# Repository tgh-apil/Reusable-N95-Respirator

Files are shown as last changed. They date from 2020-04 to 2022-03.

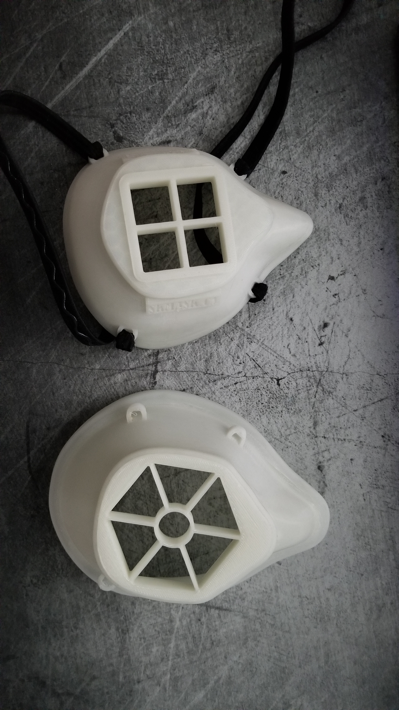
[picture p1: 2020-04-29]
02-Design Types/USask MontanaMask Mods/Photos/20200426_123736.jpg

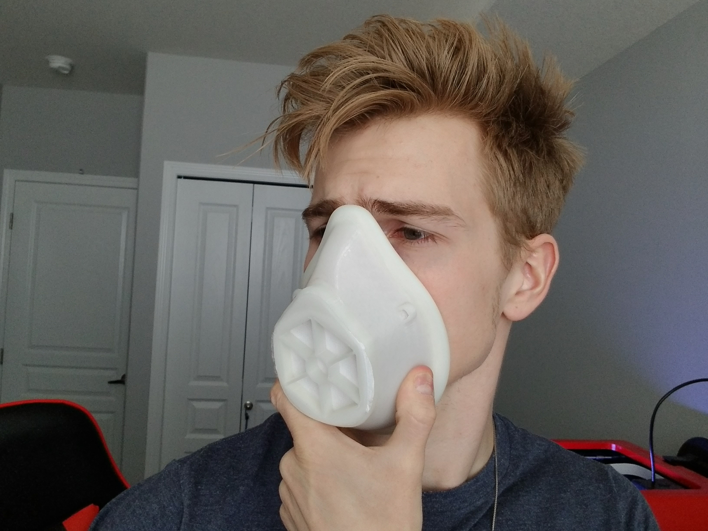
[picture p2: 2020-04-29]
02-Design Types/USask MontanaMask Mods/Photos/20200427_112252.jpg

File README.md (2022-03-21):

# Reusable N95 Respirator
An open-source, reusable N95 respirator that can be manufactured at scale in small community or hospital-based facilities, using 3D printing, silicone casting and standard HME filters.

Developed at the [Lynn & Arnold Irwin Advanced Perioperative Imaging Lab, Toronto General Hospital](https://apil.ca).

# DISCLAIMER
This is an **INVESTIGATIONAL MEDICAL DEVICE** being evaluated for use
in hospital setting during **extreme crisis** leading to N95
shortages.

It has **not been approved** by any regulatory body.

Its use is **not endorsed** by any institution or professional body,
including the ones where it was developed and tested.

We have made every effort to make the system as safe as possible and to
provide documentation and educational materials for its use, should it be
necessary, in order to minimize the very significant risks of iatrogenic harm.

It is posted here in order to facilitate rapid knowledge sharing and research
on strategies for addressing the global ventilator shortages.

Any of use of this device is done purely at your own risk and liability. The
developers and associated institutions do not accept any liability for its use.

# Publications & Media
1. [Anwari V, Ng WCK, Mbadjeu Hondjeu AR, Xiao Z, Afenu E, Trac J, Kazlovich K, Hiansen J, Mashari A. Development, manufacturing, and preliminary validation of a reusable half-face respirator during the COVID-19 pandemic. PLoS One. 2021;16(3):e0247575.](https://doi.org/10.1371/journal.pone.0247575) 
2. [Ng WCK, Hondjeu ARM, Syrett A, Caragata R, Rozenberg D, Xiao Z, Anwari V, Trac J, Mashari A. Subject validation of reusable N95 stop-gap filtering facepiece respirators in COVID-19 pandemic. PLOS ONE. 2020 Nov 13;15(11):e0242304.](https://doi.org/10.1371/journal.pone.0242304) 
3. [OCI VIP Funding Reusable N95 Respirator Report in Collaboration with TME Inc. 2021-2022](https://hackmd.io/2YckHMyaT0aIxTetDs7KHw)

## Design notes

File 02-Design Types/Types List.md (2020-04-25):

Orig: Will Ng

Last: 17 April 2020

Still nothing FDA of HC approved

# Short-list criteria
1) Open Source, licence to use and refine
2) 3D printable with available printers (to us)
3) Clinically tested 
4) Theoretically decontaminable easily
5) Theoretically suitable for long-hours wear

# Short-List
### NIH released open sources
- https://3dprint.nih.gov/collections/covid-19-response; currently only one on NIH exchange that is clinically reviewed.
- https://3dprint.nih.gov/discover/3dpx-013429 NIH "SFM" Mask is clinically tested
- many variations to choose from, apart form the above, which have gained traction and use in several hospitals
- Now modified by APIL to unibody Silicone Mould, awaiting testing.

### Simple Silicone Respirator by Christian Petropolis at HSC Manitoba
- silicone material dragon skin sx pro to 10, durometer 2A - 10
- attaches to commerical filters 15mm to 22mm
- M size fits small to large
- working copy https://cad.onshape.com/documents/a5f5de31c4732fb3c077f7d9/w/7b1df48439473aaa39a18cc3/e/e7b3ab7f8894425fe0ec1df3
- original cad https://cad.onshape.com/documents/912751c654360860ae260334/w/75644efc74b9616c5ac20c2f/e/7fecc2776bb556dd9c7c6a62
- https://github.com/cpetropolis/Simple-Silicone-Respirator

### "Kingston" Mask - Queen's Initiative
- http://ppekingston.squarespace.com/
- Modification of Montana with different sizing, filter size, geometry
- fit-testing done by OSH at KGH

### Barrow Neurosurgery
- https://www.barrowneuro.org/get-to-know-barrow/barrow-innovation-center-2/3d-printed-n95-mask/
- Montana with silicone gasket and adapter for large 3M 2000 P100 filter type

### Billings, Montana
- https://www.makethemasks.com
- tested and used Billings Clinic, MT; ? in Utah; Kaiser San Diego;

### Intermountain3D - modified Montana with flat rim
- https://www.intermountain3d.com/covid-respirators.html
- ask about files: SLS printing and assembly, lynn@intermountain3d.com

_____
## Interesting downward facing filter with screw/lock mechanism.
- https://copper3d.com/hackthepandemic/

## Other-list
- Concordia (Modified Montana) respirator mask
- https://blog.cuw.edu/access-concordias-respirator-mask-3d-print-file/
- has double inner rim, suitable for silicone/rubber gasket seal

- Basic Respirator Tyvek flat filter
- https://basicrespirator.com

## Design Partners
- Nadir Hassan, Nadir.Hassan002@gmail.com
- Jessica Schroeder, Jessica.Laura.Shcroeder@gmail.com
_____

## Government statements
FDA:
"https://www.fda.gov/medical-devices/3d-printing-medical-devices/faqs-3d-printing-medical-devices-accessories-components-and-parts-during-covid-19-pandemic"

HC: 
https://www.canada.ca/en/health-canada/services/drugs-health-products/medical-devices/covid-19-unconventional-manufacturing-personal-protective-equipment.html

CDC: 
https://www.cdc.gov/coronavirus/2019-ncov/hcp/respirators-strategy/index.html

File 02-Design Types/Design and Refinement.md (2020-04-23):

Orig: Will Ng
Last: 2020-04-21
Title: Designs and Refinements

## Manitoba Tasks
1. Harness bent-like-stool Print with cirular buttons (Arash)
2. Reduced Bottom island (Natasha)
3. All original files converted to STEP (Natasha)
4. Strap Moulds (James from Vertigro)
5. Silicone Casting (Josh and Vahid)

### Manitoba Parts
1. Manitoba Flat Harness Mould: https://a360.co/3cCDOWk (Arash)
2. Manitoba Middle Mould enlarged: https://a360.co/2xBQWfM, 2nd part file https://a360.co/2RRTo8u (Will's fault, Natasha)

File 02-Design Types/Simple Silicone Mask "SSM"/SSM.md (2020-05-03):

Orig: Will Ng
Title: Simple Silicone Mask *aka* "SSM"
Last: 2020 May 3

# Simple Silicone Mask, attribution "SSM"
## Name - "SSM"
- For simplicity we'll name this mask body design and derivatives SSM Simple Silicone Mask
- It is a branch off the Simple Silicone Respirator, which we have called "SSR"
- By itself the "SSM" body is just a mask
- A fitting filter then makes it a Respirator
- We see the future of this stop-gap solution as modular: one mask body can accommodate additional modules

# Ideas for Derviatives
## Dual Filter Cartridge
- If DAR and Intersurgical medical filters are depleted
- Having Modular FIlter solutions means we can adapt to multiple filters that can be sourced.

## Expiratory Valve
- Greatly reduces condensation, heat trap and thus improves wearer comfort
- All valves be potentially be designed with a filter so that the atmospheric air mixture droplets/particles 
is separate from inner air mixture droplets/particles.
- Awaiting Dr. Sameer Masood's design of expiratory valve with filter that can be fitted to non-rebreather masks.

## Integrated Harness
- The harness may be integrated into the body

SSM License is under the Project CERN 2.0 License so that all remain "open".

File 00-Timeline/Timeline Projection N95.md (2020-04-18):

Orig: Will Ng

Last: 17 Apr 2020

# TIMELINE for Reusable N95 Project

- Project Manager: Nasa Nguyen
- Partners: APIL, CIGITI, Lakehead, NOSM, Queen's, SickKids Anes, GLIA, UofT 3DP-GTHA, ~Brian~ (Industry)

### Lead up from 6 Apr 2020 
- NIH S, M Moulds by 10am 13 Apr 2020 [Brandon CIGITI/Will]
- Montana S, M by 10am 13 Apr 2020 [Brandon CIGITI/Will]
- NIH S, M Inlays by 10am 13 Apr 2020 [Josh/Vahid]
- see summaries and minutes on MatterMost https://group.emlondon.ca ~ "Respirator Masks"
- Choose 3 Mask bodies [Will/Andrew/Brandon/Josh/Vahid] 8pm 13 Apr 2020

### Week 1 - 13 Apr 2020
- NIOSH Testing @ 11am 13 Apr [Andrew/Vahid] [Lead/Assist]
- Adapter with slightly smaller connection to ROXON for NIH and Montana [Josh] by 14 Apr
- Bitrex Testing for 3 sizes of 1 type by 17 Apr [Andrew/Queen's]
- Bitrex Testing UHN [Will/Azad] by TBC as barriers expected
- REB [Binu/Jo Carroll] by 16 Apr
- Ontario Power Generation testing facilities [Leah|Queen's], floating
- Candidate Refining [Josh/Vahid/Brandon/Taylor] 16 Apr 
- Arrange 2nd NIOSH after refinement 17 Apr [Josh/Vahid/Brandon/Taylor]

### Week 2 - 20 Apr 2020 [Surge Week, expect Andrew, Will, Azad down]
- Decontamination Protocols [Vahid/GLIA]
- Need GLIA's help with MDEL or APIL's MDEL [Azad/GLIA]
- Health Canada approval [Azad/GLIA]
- Industry for upscale of Silicone Moulds, Bodies, [Will/Brian]
- Filtering solution from Woodbridge (if filter passes) [Will]
- First 10 units [Brian/Will]
- Test first 10 Units [Vahid/GLIA]

### Week 3 - 27 Apr 2020 [Surge Week]
- First 25 units [Brian/Will]
- Test batches [Vahid/GLIA]
- Website [other]
- Logistics [GLIA/Will]
- Dissemination of Information to interested centres [Andrew]

### Week 4 - 4 May 2020 [Surge Week]
- First 100 units [Brian/Will]
- UHN Stock for stop-gap [Will/Azad]
- Project wind-down [Will/GLIA] 
- Write-up [Andrew/Will]

### Week 5 to 8 [depending on ongoing funding]
- Reassess [All]

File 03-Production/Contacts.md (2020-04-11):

Orig: Will Ng
Last: 10 April 2020

## Materials Science
Yu Zou, PhD
- mse.zou@utoronto.ca
- Dept Materials Science and Engineering

## CIGITI, SickKids
Thomas Looi, PhD, MBA
- thomas.looi@sickkids.ca

## UHN
Tina Meisami
- tina.meisami@uhn.ca
- Sewable Mask Development

## Ostrom Medical Engineering
Devon Ostrom
- list of laser cutters and small DYI 3D printers:  http://www.osse.ca

## Industry
Woodbridge Industry and INOAC

Brian Read baread@eagle.ca
- ex-CEO of Horizons Plastics, Cobourg
- Multiple partners and contacts outside of GTA
- helped print all our samples pro bono

Andrew Pho
- FDM printers currently
- Willing to help cast mould for mass production

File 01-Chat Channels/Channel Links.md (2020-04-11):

Orig: Will Ng
Last: 10 April 2020

## PI
William Ng, UHN UofT Dept Anesthesia and Pain Management
william.ng@uhn.ca

## Coordinator
Andrew Syrett andrew.syrett@medportal.ca

## Project manager
Carla Luzzi carla.luzzi@uhn.ca

## Groups
Toronto Emergency Device Accelerator VPRI ISI Chat Channels for workflow by
Microsoft Teams. email matt.ratto@utoronto.ca

## Texting
Whatsapp groups. Text Will Ng +18573307399.

## Repository 
- for large files, such as CAD, .STL:
- https://www.dropbox.com/sh/exq93iisr1vuk3s/AACLyBetassTvupc8qk6WR29a?dl=0

## GLIA Channels for workflow 
- (NFP, medical device company partner, glia.org):
- email: jessica.laura.schroeder@gmail.com  to request

## APIL UHN lab
email: admin@apil.ca or joshua.hiansen@uhnresearch.ca

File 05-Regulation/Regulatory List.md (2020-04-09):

Title: Relevant Standards to be met and waivers requirements specified
Orig: Will Ng
Last: 8 April 2020

Health Canada
-

CSA
-

ISO
-

NIOSH
- 

HC Standards link:
https://www.canada.ca/en/health-canada/services/drugs-health-products/medical-devices/
covid-19-unconventional-manufacturing-personal-protective-equipment.html

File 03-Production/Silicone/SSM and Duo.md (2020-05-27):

Orig: William Ng
Last: 27 May 2020
Title: SSM and Duo Production Part Details

## Material
### Mask Body
- Biosafe Smooth-On inc. Dragon Skin(TM) 20

### Straps
- Dragon Skin 10
- Alternative sourced OTS hole-punched straps from Amazon or Alibaba

### Harness
- PLA print in 3D
- Could be flat print then thermoset

### Filter
- Intersurgical AirGuard for SSM (HEPA)
- Intersurgical HydroMini for Duo x 2 (HEPA, ~ 1/2 surface area of AirGuard)

## Valve Adapters for Duo
### Umbrella Valves
- 2 inspiratory valves (larger)
- 1 expiratory (smaller)
- cheap to source in large volumes

### Seat
- high res print on stratasys
- currently whole adapter including seat printed on high res, print adjusted to valve sizes

### Adapter tube
- low res print
- seat can be press-fit into tube +/- glue

## Future design
- Silicone Gasket
- 3DP body with harness hooks or strap holders

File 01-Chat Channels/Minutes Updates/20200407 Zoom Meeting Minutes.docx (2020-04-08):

April 7th Zoom Meeting Minutes

Attendees:

- William Ng
- Azad Mashari
- Andrew Syrett
- Vahid Anwari
- Matt Ratto
- Brian Read
- Brian Clarkson

Status of Prototypes

1. I3D models in TGH team’s hands, worn/comfort tested by various members. Have window weather stripping as seal. Firm, and may become uncomfortable with prolonged use
2. B1/B2 model (same as 13D but from different machine) to be delivered to TGH today

Will NG discussed new open source model from University of Washington/Veteran’s hospital approved by NIH. We would like to try this model, as it has a larger filter, which would reduce wearer’s work of breathing. We will call this model “NIH”. Brian’s team to produce a prototype today. Vahid will be in contact to share CAD files.

Main Issues:

1. Seal and comfort. We need to find a solution given that the mask material is so firm – prolonged use will cause skin ulceration.
  a. Possible solutions proposed:
    i. Extruded silicone to fit around edge of mask (would require that seam be “welded” so as to prevent air leak
    ii. Room temperature vulcanization process whereby silicone would be adhered directly to edge of mask.
    iii. Rubber silicone tubing, with a slit cut through it, and wrapped onto edge of mask, which would represent a DIY option
  b. Plan:
    i. Brian R and Brian C will look into extruded silicone and RTV options in their circles
    ii. Matt R will liaise with Acro Industries re. extruded silicone
    iii. Vahid/Josh will look into sourcing silicone tubing
  c. Issues: some of these solutions may need tweaking of the prototypes to include a lip onto which seal material can be affixed.
2. Filter. We need to find a filter solution that is easily sourced and readily available
  a. Possible solutions - Halyard surgical sterilization wrap sandwiched around HEPA filter material.
    i. Halyard wrap abundant at TGH and most hospitals. We have some in the lab for testing purposes
    ii. Matt R to liaise with contacts at Camfil to obtain HEPA material.
  b. Issues: will need to seal/adhere the 3-ply sandwich around the perimeter of each filter. May be possible to use a heat source to bond them together.

Actions to be taken:

1. Will/Azad/Andrew to coordinate grant writing
2. Vahid/Josh to coordinate lab, collecting and preparing prototypes and to source silicone tubing
3. Matt R to liaise with industry partners at Acro and Camfil
4. Matt R to help connect us with testing partners
5. Brian R and Brian B to help with production of NIH prototype, and to investigate feasibility of extruded silicone and RTV seal options.

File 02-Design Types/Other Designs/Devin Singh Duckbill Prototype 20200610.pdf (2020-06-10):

## Duckbill Dev Mask Homebrew 0.4 / DD70

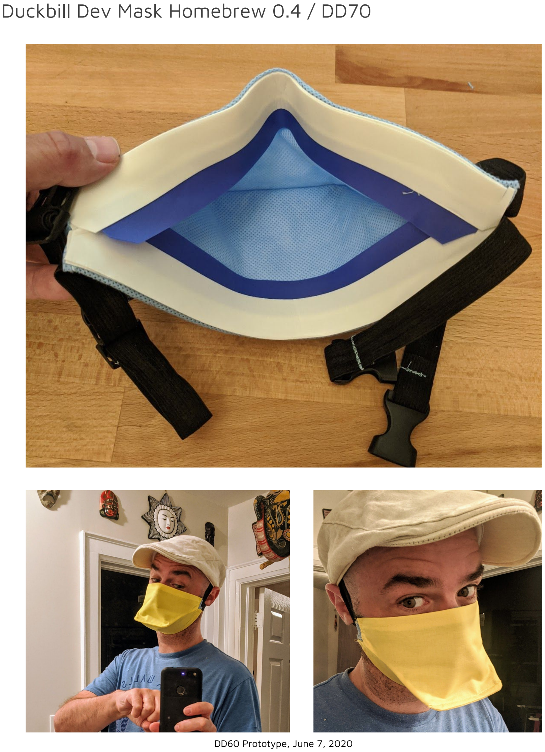
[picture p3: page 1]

DD60 Prototype, June 7, 2020

## Work In Progress Features: Duckbill Dev V0.4 / DD70

Filtration:
- Large filtration area for resisting moisture / easing breathing comfort (+/- 256 cm2) x2 Layers AdvanCheck, SMS Barrier Autoclave Wrap (https://advantechsterilizers.ca/product/advancheck-sms-autoclave-wrap-24-in-x-24-in/) to resist moisture saturation.
x1 Layer Filti Nano Fabric (https://filti.com/product/filti-face-mask-material/)
x1 Layer tight weave Kona Cotton Fabric (https://www.etsy.com/transaction/1922363445?email_sent=1591211329&euid=xRHRHhk-HQW7lMo60ahNOIko_PRf&eaid=23368334549&x_eaid=db79cf65fc&link_clicked=9) exterior to reduce virus lifespan.
- Estimated current filtration in 70-80% of 0.3 micron particles (https://docs.google.com/spreadsheets/d/17aJQn-zmhBWO9vlgfWQLAuRUNrxrUnE8Ftm2wUHlddI/edit?usp=sharing) (not including double surface area.)

Fit:
- ‘Skin safe’ silicone tape + nitrile tourniquet face seal on interior.
- Quick release snaps to ease safe donning / doffing / neck resting.
- Dual integrated ¾” elastic with overlap at corners.
- Heavy file binder nose piece.

Notes / Next Version:
- Add painted on nostrils to improve comedic potential.
- Separate cotton cover and straps for ease of cleaning / re-use.
- Include cotton layer on interior to reduce respiratory irritation.
- Consider salt layer
- Make goose and duckling versions.
- Add electrostatic layer.
- Improve nose seal bridge.

Base Pattern Here, Elaboration on Design by Dr. Chris Holmes https://www.instructables.com/id/Face-Mask-Duckbill-With-Filter/

Inquiries:
devon@ostrom.ca Last Edit, June 9 2020 https://tinyurl.com/devduckbill

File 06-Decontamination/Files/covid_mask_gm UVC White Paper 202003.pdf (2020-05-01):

Maintaining adequate supply of N95 filtering facepiece respirators (FFRs) during a shortage by safely decontaminating and reusing equivalent alternatives Jacob Bender, Dr. Azad Mashari, Dr. Tarek Loubani

Highlights

1. Disposable N95 filtering facepiece respirators (FFRs) are expected to be, and in some cases already are, in short supply during the ongoing SARS-CoV-2 pandemic¹
2. Filters that offer NIOSH-approved N95 filtering capacity exist in other fields of work such as the automotive and construction industries and may still be available from commercial suppliers²,3 even when medical supply is used up. These filters are used in conjunction with a reusable silicone facepiece that is easily sterilized with hypochlorite solution⁴
. These reusable silicone facepieces, (“masks”), are approved for use in industrial applications with far more stringent particulate and vapour-filtering requirements than disposable N95 FFRs commonly used in healthcare.
3. UV germicidal irradiation (UVGI) and dry heat treatment⁵,6 are accessible, inexpensive, and reasonable means of decontaminating the filters without compromising their filtering capacity⁷⁻⁹
4. We offer a review of current knowledge on this subject and a framework for hospitals and health care providers to follow that includes the use of reusable facepieces in conjunction with filters that can be decontaminated in order to conserve resources in a time of need such as the ongoing SARS-CoV-2 pandemic.
5. It is very possible that with proper handling procedures these reusable masks may prove superior both in terms of performance and cost compared to disposable FFRs and may warrant adoption for use beyond the duration of the current pandemic.

Introduction

N95 FFRs remain the personal protective equipment (PPE) of choice to mitigate exposure to airborne pathogens. The Centers for Disease Control and Prevention (CDC) and the Public Health Agency of Canada (PHAC) specifically recommend this as the PPE to control exposure of care providers from patients with suspected or confirmed Severe Acute Respiratory Syndrome Coronavirus 2 (SARS-CoV-2) infection¹⁰,11. A shortage of N95 FFRs is a major concern of health care experts and practitioners during viral respiratory illness pandemics¹². The H1N1 pandemic of 2009 demonstrated how quickly stores of PPE, specifically FFRs, can become exhausted¹

The ongoing SARS-CoV-2 pandemic has led to N95 FFR shortages around the world. The CDC has suggested a framework of optimizing supplies and mitigating shortages. The CDC defines three specific situations relating to the capacity of a health care settings involved in treating conditions requiring the use of N95 FFRs: (1) conventional capacity; (2) contingency capacity, and (3) crisis capacity. Contemporary practice of disposable FFR use dictates that health care providers (HCPs) doff and discard masks after exiting a patient room and closing the door. In a pandemic situation, this practice pattern can result in rapid consumption of FFR reserves. The CDC suggests that HCPs maintain daily contemporary practices with regard to FFR use during a period of conventional capacity, until a situation such as the ongoing pandemic, at which point more advanced measures may be taken. They suggest that at contingency capacity, measures may be taken to change daily contemporary practices, but must not have a significant impact on care delivered or safety of the HCP; importantly, they suggest that these practices may be used temporarily when demand exceed resources. When faced with crisis capacity (an extended period where demand exceeds resources), such as the ongoing SARS-CoV-2 pandemic, the CDC suggests that “alternate strategies not commensurate with contemporary U.S. standards of care may be employed”. These measures may need to be considered during periods of expected or known N95 respirator shortages¹³.

The CDC elaborates on two measures aimed at optimizing inventory of FFRs: (1) extended use of FFRs, such that FFRs are not removed between individual patient interactions; and (2) reuse of FFRs, such that they are donned before and doffed after each interaction¹⁴. The reuse and extended use of FFRs reasonably reduce FFR consumption, but also come with downsides:
- Risk of contamination by touching the reused FFR when donning and doffing, followed by self-inoculation through touching one’s own mucous membranes or indirect/direct transmission to others¹⁵;
- Concomitant contamination of FFR with other pathogens acquired from patients; and
- Reduction in the respirator’s ability to filter effectively due to excessive use¹⁶

Even though reuse and extended use measures aim to reduce the number of disposed-of FFRs, they do not fully solve the issue of sustainability in a situation where new FFRs are not being restocked at adequate rates because of worldwide shortages. Because of this, decontamination or sterilization of FFRs for reuse has been a topic of great interest throughout this current pandemic. HCPs are exploring sterilization of disposable FFRs using heat, liquid disinfectants such as isopropyl alcohol or chlorine-containing solutions, microwave-generated steam, or UVGI. A 2012 study suggests that UVGI was superior over microwave-generated steam and moist heat for decontaminating N95 masks from influenza⁹
. A 2004 study showed that the coronavirus responsible for causing SARS-CoV was completely inactivated after being subjected to 75ºC for 45 minutes⁵
. Dr. Liu Haixa, a doctor from Beijing, found that spraying masks with liquid disinfectant and autoclaving the masks reduced their filtering capacity to below 95%, while UVGI and dry heat (70ºC for 30 minutes) did not degrade filtering capacity¹⁷. Another study suggests only a modest increase (up to 1.25%) in particle penetration of N95 filters when the filters were subjected to germicidal levels of UVC radiation⁷
. Yet another study
suggests no increase in aerosol penetration when treating filters with germicidal levels of UVC radiation⁸
. Coronaviruses are susceptible to destruction by UVGI, and SARS-CoV-2 is no exception¹⁸. Germicidal UV-C lamps are available from commercial sources¹⁹, as well as pet stores as the lamps are also used to sterilize aquarium water.

Other industries use respiratory protection for their workers, such as automotive painters, welders, and construction workers. Filters that are more amenable to sterilization already exist, such as the 3M 5N11² and the 3M 5P71³
, which offer NIOSH-certified N95 and P95 protection, respectively. These filters are used in conjunction with adaptors (such as the 3M 603²⁰), a filter retainer (such as the 3M 501²¹), and a reusable facepiece (such as the 3M 7500 series²² or 3M 6000 series²³), which themselves can be individually sterilized, which is particularly important where the device may have been contaminated with SARS-CoV-2⁴
. In the case of a shortage of reusable adaptors and retainers, 3D-printed replacements can be easily and cheaply made and distributed²⁴⁻²⁶.

Sterilization procedures based on currently available evidence

We have tested the procedures below with the following equipment without any loss of device integrity. We were not able to test for residual viral activity post-procedure.

Mask: 3M model 7502 half facepiece reusable respirator, size medium²². The 6500-series half facepiece reusable respirators similar in function.

Particulate filters: 3M model 5P71 particulate filter, P95¹⁵
Associated supplies: 3M model 501 prefilter retainer²¹ & 3D printed alternative²⁵, 3M model 603²⁰ & 3D printed alternatives²⁴,25.

Cleaning solution for facepiece: 5,000ppm free chlorine solution⁴
. Use Public Health Ontario’s Chlorine Dilution Calculator²⁷ for sodium hypochlorite (bleach) or Glia’s ChlorineCalc²⁸ for calcium hypochlorite granules.
Decontamination device: 16L UV sterilizer, 6W UV-C, 200W heating element²⁹.

Reusable facepiece, 501 prefilter retainer, and 603 adaptor decontamination protocol: Facepiece, retainer, and adaptor were soaked in solution with 5,000ppm free chlorine for one minute⁴
. They were then rinsed with water and hung to dry.

Particulate filter decontamination protocol – UVGI & heat:

Always ensure that the decontamination device is OFF prior to opening the door. When on, the UVC light is harmful to your skin if directly exposed, as well as harmful to look at directly.

The inside of the decontamination device and the stainless-steel basket were cleaned with 5,000ppm free chlorine solution. The removable stainless-steel basket was removed from the decontamination device. The particulate filters were placed into the basket with the side labelled “mask side” face-down. The device was then turned on and left for 60 minutes. The temperature was monitored and maintained a temperature above 70ºC for the 60 minutes. At 60 minutes, the device was switched off. The door to the device was opened and the interior was allowed to cool for ten minutes. The basket and filters were then removed in a clean fashion using clean nonsterile gloves after they had cooled enough to handle safely. The filters maintained their structural integrity and were not visibly different compared to when new.

If filters are visibly soiled, or if they make breathing through the reusable facepiece difficult, they may need to be replaced. Ensure that the interior surface of the heated device is decontaminated with 5,000ppm free chlorine solution both prior to and after heat decontamination of the filters. After decontamination, inspect the filters for any signs of physical degradation. If the filters appear to be losing their structural integrity, they may need to be replaced.

Conclusion

We propose a more sustainable framework for respirator use to be employed during periods of disposable FFR shortage, such as the ongoing SARS-CoV-2 pandemic. This framework conforms to CDC¹⁰ and PHAC¹¹ guidelines relating to PPE use with airborne and droplet precautions as the materials proposed already have NIOSH ratings for N- and P95 filtering capacity. The decontamination protocol of the reusable facepiece is published by the manufacturer specifically for those contaminated by coronavirus⁴
. The decontamination
protocols for the filters are based on previous research in this field specific to coronaviruses and other viral agents. Dry heat is recognized as a reasonable means of inactivating the virus if treated for 45 minutes at 75ºC, which is easily achieved with a household slow cooker or rice cooker. The literature on UVGI suggest that it is an effective means of decontamination with low impact on filtering capacity⁷⁻⁹
. There are devices that combine the two modalities of decontamination that are commercially available and can be easily deployed in a health care setting²⁹.

References

1. Rebmann T, Wagner W. Infection preventionists’ experience during the first months of the 2009 novel H1N1 influenza A pandemic. Am J Infect Control. 2009;37(10):e5-e16. doi:10.1016/j.ajic.2009.09.003
2. 3M. 3MTM Particulate Filter, 5N11, N95, 50 pairs/case. https://www.3mcanada.ca/3M/en_CA/company-ca/all-3m-products/~/3M-Particulate-Filter-5N11-N95-50-pairs-case/?N=5002385+8711017+3293806364+3294529206&rt=rud. Accessed March 20, 2020.
3. 3M. 3MTM Particulate Filter, 5P71, P95, 50 pairs/case. https://www.3mcanada.ca/3M/en_CA/company-ca/all-3m-products/~/3M-Particulate-Filter-5P71-P95-50-pairs-case/?N=5002385+8711017+3293806346+3294529206&rt=rud. Accessed March 20, 2020.
4. 3M Personal Safety Division. Cleaning and Disinfecting 3M Reusable Elastomeric Half and Full Facepiece Respirators following Potential Exposure to Coronaviruses. :3.
5. Darnell MER, Subbarao K, Feinstone SM, Taylor DR. Inactivation of the coronavirus that induces severe acute respiratory syndrome, SARS-CoV. J Virol Methods. 2004;121(1):85-
91. doi:10.1016/j.jviromet.2004.06.006
6. Kariwa H, Fujii N, Takashima I. Inactivation of SARS Coronavirus by Means of Povidone-Iodine, Physical Conditions and Chemical Reagents. Dermatology. 2006;212(1):119-123. doi:10.1159/000089211
7. Lindsley WG, Jr SBM, Thewlis RE, et al. Effects of Ultraviolet Germicidal Irradiation (UVGI) on N95 Respirator Filtration Performance and Structural Integrity. J Occup Environ Hyg. 2015;12(8):509-517. doi:10.1080/15459624.2015.1018518
8. Viscusi DJ, Bergman MS, Eimer BC, Shaffer RE. Evaluation of Five Decontamination Methods for Filtering Facepiece Respirators. Ann Occup Hyg. 2009;53(8):815-827. doi:10.1093/annhyg/mep070
9. Lore MB, Heimbuch BK, Brown TL, Wander JD, Hinrichs SH. Effectiveness of three decontamination treatments against influenza virus applied to filtering facepiece respirators. Ann Occup Hyg. 2012;56(1):92-101. doi:10.1093/annhyg/mer054
10. CDC. Infection Control: Severe acute respiratory syndrome coronavirus 2 (SARS-CoV-2) | CDC. https://www.cdc.gov/coronavirus/2019-ncov/infection-control/control-
recommendations.html?CDC_AA_refVal=https%3A%2F%2Fwww.cdc.gov%2Fcoronaviru s%2F2019-ncov%2Fhcp%2Finfection-control.html. Accessed March 19, 2020.
11. Public Health Agency of Canada. Infection prevention and control for coronavirus disease (COVID-19): Interim guidance for acute healthcare settings. aem. https://www.canada.ca/en/public-health/services/diseases/2019-novel-coronavirusinfection/health-professionals/interim-guidance-acute-healthcare-settings.html#a4.10. Published February 24, 2020. Accessed March 19, 2020.
12. WHO. Shortage of personal protective equipment endangering health workers worldwide. https://www.who.int/news-room/detail/03-03-2020-shortage-of-personal-protectiveequipment-endangering-health-workers-worldwide. Accessed March 19, 2020.
13. CDC. Strategies for Optimizing the Supply of N95 Respirators. Centers for Disease Control and Prevention. https://www.cdc.gov/coronavirus/2019-ncov/hcp/respiratorsstrategy/index.html. Published February 11, 2020. Accessed March 19, 2020.
14. CDC. Recommended Guidance for Extended Use and Limited Reuse of N95 Filtering Facepiece Respirators in Healthcare Settings. https://www.cdc.gov/niosh/topics/hcwcontrols/recommendedguidanceextuse.html. Published March 9, 2020. Accessed March 19, 2020.
15. Rebmann T, Carrico R, Wang J. Physiologic and other effects and compliance with longterm respirator use among medical intensive care unit nurses. Am J Infect Control. 2013;41(12):1218-1223. doi:10.1016/j.ajic.2013.02.017
16. Fisher EM, Shaffer RE. Considerations for Recommending Extended Use and Limited Reuse of Filtering Facepiece Respirators in Health Care Settings. J Occup Environ Hyg. 2014;11(8):D115-D128. doi:10.1080/15459624.2014.902954
17. Haixa L. Can disposable masks be reused after sterilization? WeChat Official Accounts Platform.
http://mp.weixin.qq.com/s?__biz=MjM5ODUwMDkwOQ==&mid=2660201753&idx=1&sn=b5b7d5c25e00ffb684ff52f3f242c6fb&chksm=bdb21a5b8ac5934dc5b7d11ef71ea153a5c 4771777feb1ec505bb655254fcaf741443cd0edfb#rd. Accessed March 19, 2020.
18. Cascella M, Rajnik M, Cuomo A, Dulebohn SC, Di Napoli R. Features, Evaluation and Treatment Coronavirus (COVID-19). In: StatPearls. Treasure Island (FL): StatPearls Publishing; 2020. http://www.ncbi.nlm.nih.gov/books/NBK554776/. Accessed March 19, 2020.
19. Amazon. Amazon.ca: uvc bulb. https://www.amazon.ca/s?k=uvc+bulb&ref=nb_sb_noss_2.
20. 3M. 3MTM Filter Adapter, 603, 16/case. https://www.3mcanada.ca/3M/en_CA/workerhealth-safety-ca/products/~/3M-Filter-Adapter-603-16-case/?N=5011378+3292220856+3294529206&rt=rud. Accessed March 20, 2020.
21. 3M. 3MTM Retainer, 501, 20/pack. https://www.3mcanada.ca/3M/en_CA/company-ca/all-3m-products/~/3M-Retainer-501-20-pack/?N=5002385+8711017+3293806390+3294529206&rt=rud. Accessed March 20, 2020.
22. 3M. 3MTM Half Facepiece Resuable Respirator, 7502, medium, 1/bag. https://www.3mcanada.ca/3M/en_CA/company-ca/all-3m-products/~/3M-Half-Facepiece-

Resuable-Respirator-7502-medium-1-bag/?N=5002385+8711017+3293806334+3294529206&rt=rud. Accessed March 20, 2020.

23. 3M. 3MTM Half Facepiece Resuable Respirator, 6200, medium, 24/case. https://www.3mcanada.ca/3M/en_CA/company-ca/all-3m-products/~/3M-Half-Facepiece-Resuable-Respirator-6200-medium-24-case/?N=5002385+8711017+8720550+3293806388+3294529206&rt=rud. Accessed March 20, 2020.
24. Thingiverse.com. 3M 603 Filter mount by digitallee. https://www.thingiverse.com/thing:4219178. Accessed March 20, 2020.
25. Thingiverse.com. Dust filter cover for 3M mask by vyrobca. https://www.thingiverse.com/thing:3982639. Accessed March 20, 2020.
26. Thingiverse.com. 3M 603 FILTER ADAPTER by vyrobca. https://www.thingiverse.com/thing:4215903. Accessed March 20, 2020.
27. Chlorine Dilution Calculator. Public Health Ontario. https://www.publichealthontario.ca/en/Health Topics/Environmental Occupational Health/Water Quality/Chlorine Dilution Calculator. Accessed March 22, 2020.
28. ChlorineCalc. https://gliax.github.io/chlorine-calculator/. Accessed March 25, 2020.
29. GreenLife® Towel Warmer with UV Sterilizer (16L, White): Amazon.ca: Beauty. https://www.amazon.ca/gp/product/B07PPWWRN7/ref=ppx_yo_dt_b_asin_title_o00_s00?ie=UTF8&psc=1. Accessed March 25, 2020.

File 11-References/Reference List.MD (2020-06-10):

Orig: Will Ng

Last: 10 Jun 2020

Title: Reference List

# References

1. National Academies of Sciences, Engineering, and Medicine; Health and Medicine Division; Board on Health Sciences Policy; Committee on the Use of Elastomeric Respirators in Health Care; Liverman CT, Yost OC, Rogers BME, et al., editors. Reusable Elastomeric Respirators in Health Care: Considerations for Routine and Surge Use. Washington (DC): National Academies Press (US); 2018 Dec 6. 2, Elastomeric Respirators. Available from: https://www.ncbi.nlm.nih.gov/books/NBK540078/

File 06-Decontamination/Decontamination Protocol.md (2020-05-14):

Original: William Ng

Last: 13 May 2020

Thanks: Jake Bender and Tarek Loubani's white paper in Mar 2020

Aim: Adapt to institutional requirement

# References

1. Centers for Disease Control and Prevention (CDC). Strategies for Optimizing the Supply of Facemasks. 2020;Available from https://www.cdc.gov/coronavirus/2019-ncov/HCW/ppe-strategy/face-masks.html.

2. The Centers for Disease Control and Prevention. Strategies for Optimizing the Supply of N95 Respirators: Contingency Capacity Strategies. Available Httpswwwcdcgovcoronavirus2019- NcovHCWrespirators-Strateg-Capacity-Strateg. February 2020.

3. Chief Medical Officer of Health (CMOH), Ministry of Health (MOH), Ministry of Labour, Training and Skills Development (MLTSD), and ONA. Joint Statement: COVID-19 and Health and Safety Measures, including Personal Protective Equipment. http://www.health.gov.on.ca/en/pro/programs/publichealth/coronavirus/ 2019_covid_joint_statement.aspx.

4. Bailar, J et al. Reusability of Facemasks During an Influenza Pandemic: Facing the Flu. Wash DC IOM Natl Acad Press 2006.

5. Radonovich L et al. Better Respiratory Equipment using Advanced Technologies for Healthcare Employees (Project BREATHE): a Report of an Interagency Working Group of the U.S. Federal Government: U.S. Dept of Veterans Affairs. 2009.

6. Prepared by Battelle Columbus, Ohio. Prepared under, 135 Contract No. HHSF223201400098C. Study Number 3245. Prepared for the FDA. July. Final Report for the Bioquell Hydrogen Peroxide Vapor (HPV) Decontamination for Reuse of N95 Respirators. https://www.fda.gov/media/136386/download.

7. Schwartz, A et al. Decontamination and Reuse of N95 Respirators with Hydrogen Peroxide Vapour to Address Worldwide Personal Protective Equipment Shortages During the SARS-CoV-2 (COVID- 19) Pandemic. Https://www.safety.duke.edu/sites/default/files/N-95VHP-Decon-Re-Use.pdf.

8. Ikarashi Y, Tsuchiya T, Nakamura A. Cytotoxicity of medical materials sterilized with vapour-phase hydrogen peroxide. Biomaterials. 1995;16(3):177-183.

9. 29 CFR 1910.1000 TABLE Z‐1 ‐ TABLE Z‐1 Limits for Air Contaminants. https://www.osha.gov/laws‐regs/regulations/standardnumber/1910/1910.1000TABLEZ1

10. 3M technical bulletin. Disinfection of Filtering Facepiece Respirators. Httpsmultimedia3mcommwsmedia1816576Odisinfection--Dispos-Respir-Tech-Bull. March 2020. https://multimedia.3m.com/mws/media/1816576O/disinfection-of-disposable-respirators-technical- bulletin.pdf. Accessed March 31, 2020.

11. Hinton D. Letter from Dr. Denise M Hinton, chief scientist of the FDA to Mr. Jeff Rose of Battelle Memorial Institute. March 2020.

12. Loubani T. Health care workers must move to reusable respirators now: Here’s how. Https://mediumcomtrklouhealth-Care-Work-Must-Move--Reusable-Respir--Heres--33708ce0cd93. March 2020.

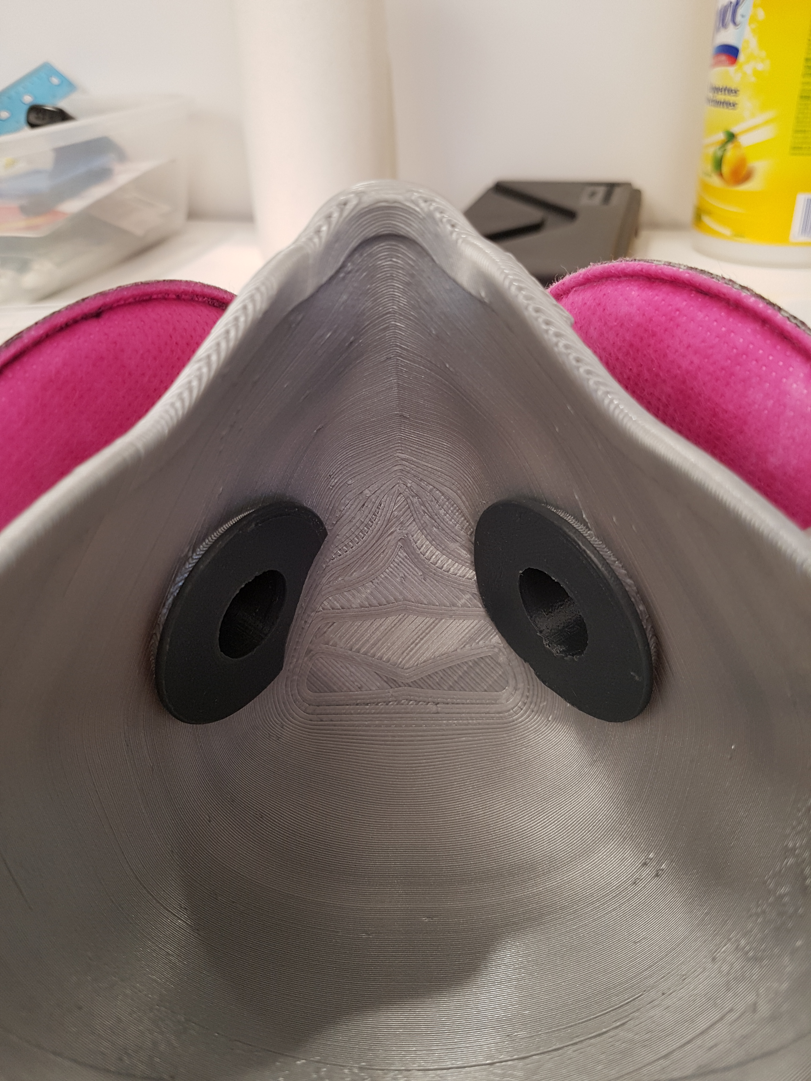
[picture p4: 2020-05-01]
02-Design Types/Other Designs/Bayonet Adapters/Andre's Mod/3M 2000 filter bayonet 2.jpg

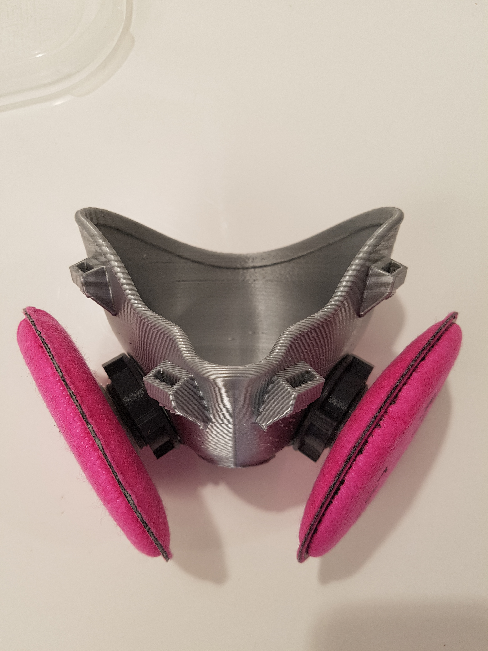
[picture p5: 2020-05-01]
02-Design Types/Other Designs/Bayonet Adapters/Andre's Mod/3M 2000 filter bayonet 1.jpg

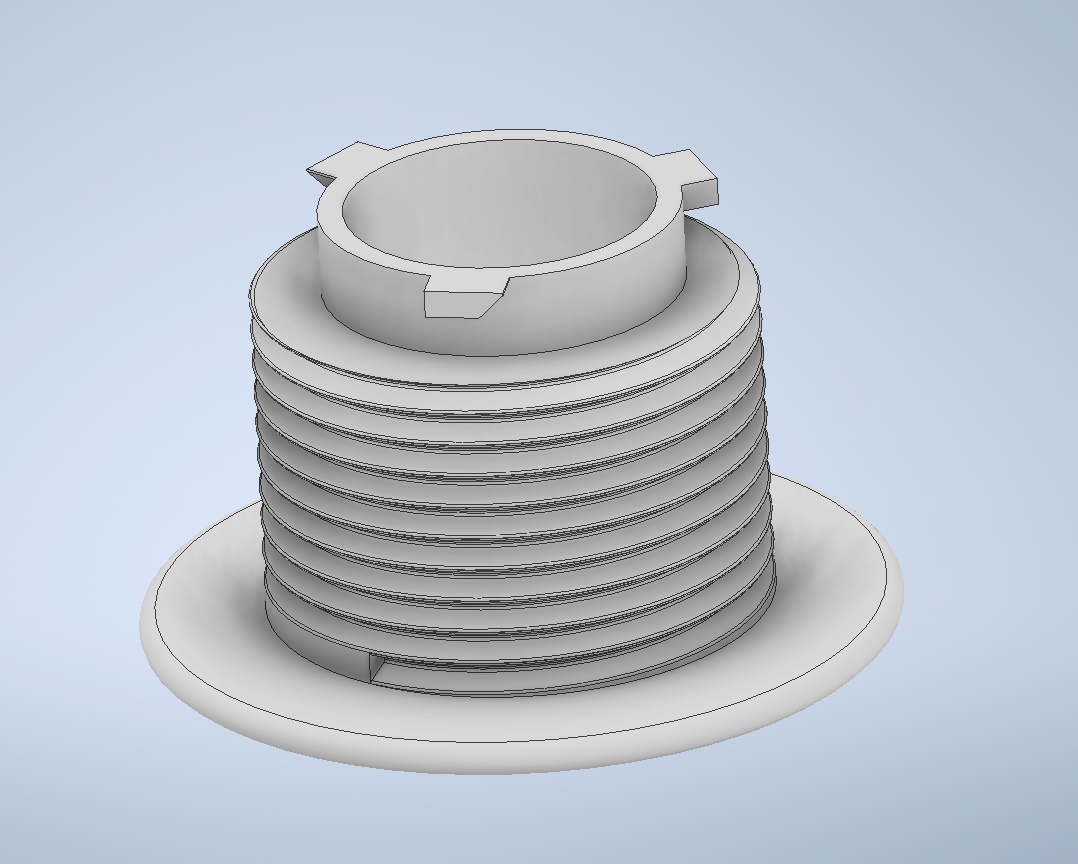
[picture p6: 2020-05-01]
02-Design Types/Other Designs/Bayonet Adapters/Andre's Mod/Bayonet 4.png

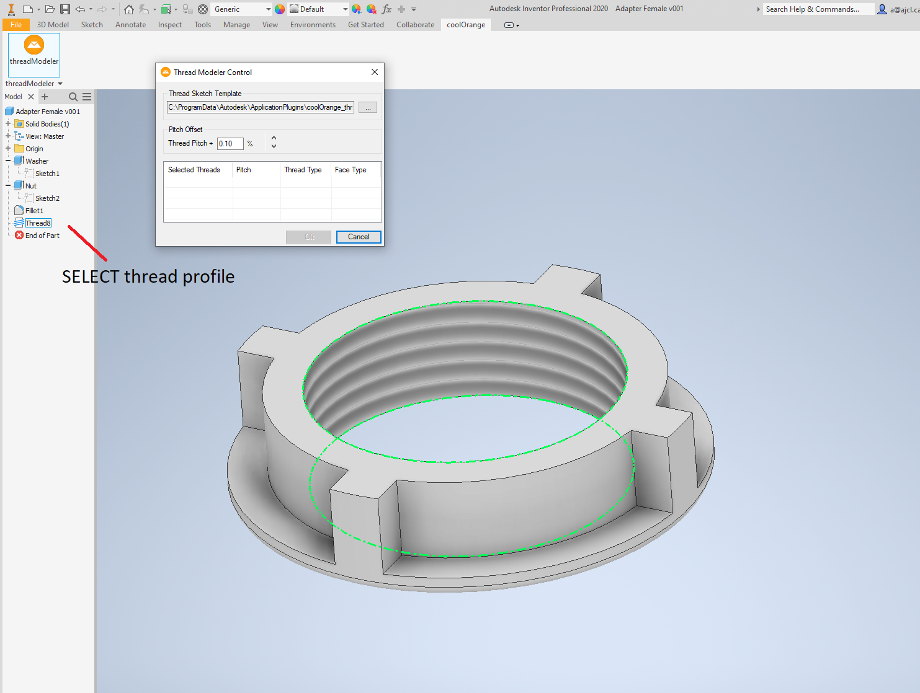
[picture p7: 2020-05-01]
02-Design Types/Other Designs/Bayonet Adapters/Andre's Mod/Bayonet 2.png

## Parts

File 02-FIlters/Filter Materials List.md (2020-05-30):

Orig: Will Ng

Title: Filter Materials List

Last: 30 May 2020

[Master Sheet]()

# Filter by Locator
## Quang Nguyen
- KEEP6W (China)
- VACURAMA
- Surgimask (VN)
- Surgimask (CN)

## Queen's
- Billings MERV-14
- McMaster MERV-15 

## UofT
- Halyard H100
- Halyard H300
- Halyard H400
- Halyard H600
- Woodbridge INOAC N95 5-ply

## UHN
- H&V MERV-14
- Camfil Hepa Filter Paper
 
## Lakehead
- Rig10
- Bootie
- Containe Filter Black and Red Tabs
- Yellow Pad (MERV 8? - TBC)
- Vestex Mask

## Other
- 3M N95 mask
- 3M 5N11 (white)
- 3M 2000 series (pink)

## Filter xlsx 2020.05.30
### Filter	FiltrationFactor	LabelsofFilter
- N95 NIOSH Moldex	162.86	
- 3M 5N11	2330.88	
- CamFilMERV15-1Ply	52.72	
- CamFilMERV15-2Ply	603.56	
- WoodbridgeINOAC-5Ply	287.06	
- H400-2Ply	31.53	Halyard400
- H100-2Ply	28.41	Halyard100
- KingstonMERV15-1Ply	142.73	
- BillingsMERV14-1Ply	59.20	
- BillingsMERV14-2Ply	474.97	
- HVMERV14-1Ply	43.33	
- HVMERV14-2Ply	264.38	
- HVMERV14+H100-1Ply	117.96	
- HVMERV14+H300-1Ply	744.65	
- HVMerv14+H300-2ply	1540.09	
- HVMerv14+H400-1ply	1221.97	
- HVMerv14+H400-2ply	7883.12	
- Q-1-1Ply	897.85	KEEP6W-China
- Q-2-1Ply	67.04	VACURAMA-Amazon
- Q-3	1154.21	VACURAMA-Amazon-with2middlelayers
- Q-4	8.17	Surgimask-VN
- Q-5	14.86	Surgimask-CN
- Ridg10	11.23	
- Bootie	3.82
- ContaineFilterBlackTab	4.74	
- ContaineFilterRedTab	4.34	
- YellowPad-(1layer)	29.37	
- YellowPad-(2layer)	244.89	
- VestexMask	1.77

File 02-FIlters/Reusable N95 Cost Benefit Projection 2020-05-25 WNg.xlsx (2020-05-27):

Projected Cost-Benefit of SSM, SSM Duo, CAD per unit |  |  |  |  | Time to set is ~3 h
William C. K. Ng 2020 May 25
 |  | Filter life can be prolonged in disaster |  |  | Note Time decreases with more moulds
SSM | Materials | Filter (1) | Filter Life (d) | Labour | Time/8 moulds (h) | Days | Needs | Unit Cost | Cost per wear 1 month | Incl. Overheads 20% | Uses per Mask | Valve Life
100 Units | 12 | 3.6 | 2 | 10 | 3 | 6 | 1 tech | 25.6 | 2.53 | 3.04 | 100 | NA
500 Units | 8 | 3.6 | 2 | 9 | 3 | 14 | 2 techs | 20.6 | 2.37 | 2.84 | 100 | NA
1000 Units | 6 | 3.5 | 2 | 10 | 3 | 20 | 3 techs | 19.5 | 2.28 | 2.74 | 100 | NA
 |  |  |  |  |  |  |  | 0
SSM Duo | Materials | Filters (2) | Filter Life (d) | Labour | Time/8 moulds (h) | Days | Needs | 0 | Cost per wear 1 month | Incl. Overheads 20% | Uses per Mask | Valve Life (d) | Valve cost
100 Units | 16 | 4.1 | 5 | 15.5 | 3 | 6 | 1.5 techs | 35.6 | 2.01 | 2.41 | 100 | 100 | 0.05
500 Units | 12 | 4.1 | 5 | 12 | 3 | 14 | 2.5 techs | 28.1 | 1.76 | 2.11 | 100 | 100 | 0.05
1000 Units | 10 | 4 | 5 | 12 | 3 | 20 | 3.5 techs | 26 | 1.67 | 2.00 | 100 | 100 | 0.05
SSM strength |  | SSM challenge
Reusable |  | Requires donning and doffing
Decontaminable |  | Requires Filter
Becomes personal property
SSM Duo Strength |  | SSM challenge
Decrease work of breathing |  | Requires donning and doffing
Increase Filter-Life |  | Requires Surgical Mask or built-in filter on expiratory valve
Less heat moisture retention
Better Audio quality
Easier for Face-Shields

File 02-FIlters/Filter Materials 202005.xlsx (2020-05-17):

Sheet: Materials
Material Mastersheet
Updated | 2020-05-04
Updater | Will Ng
Site | No. | Filter | Company | Thickness | Appearance | Plies in Pack | Origin | Cost | Woven | Comment | Web-Link
Lakehead |  | Bootie | Medi-Select | <1mm | Blue | 1 | China |  | 1 | Shoe-Cover Ref CCTS-R | www.medi-select.ca
 |  | MERV-8 Enduropleat |  |  | wired
 |  | MERV-8 Aerostar |  |  | wired
 |  | Ridg10 |  |  | green
 |  | Containe Filter |  |  | red-tab |  |  |  |  | unprocessed
 |  | Containe Filter |  |  | black-tab |  |  |  |  | processed
Quang | Q-1 | Small vacuum bag | KEEPW6 | 1 | white | 3 | Amazon |  | 1 | 2 woven & 1 hepa filter
 | Q-2 | vacuum bag | VACURAMA | 1 | white | 3 | VACURAMA |  | 1 | 2 woven & 1 hepa Filter | vacurama.com
 | Q-3 | vacuum bag | VACURAMA | 2 | white | 4 | VACURAMA |  | 1 | 2 woven & 2 hepa filters | vacurama.com
 | Q-4 | surgimask | N/A | 1 | blue | 1 | Vietnam |  | 1 | surgimask
 | Q-5 | surgimask | N/A | 1 | blue | 1 | China |  | 1 | surgimask
UHN |  | H100 | Halyard | <1mm |  |  |  |  | 0
 |  | H300 | Halyard | <1mm |  |  |  |  | 0
 |  | H400 | Halyard | <1mm |  |  |  |  | 0
 |  | H600 | Halyard | <1mm |  |  |  |  | 0
UofT |  | MERV-14 | H&V | 2mm | clear-white | 1 |  |  | 0
 |  | Hepa Paper |  | <1mm | white |  |  |  | 0 | fibre-glass
Queen's |  | MERV-14 "Billings" | TBC | 2mm | green | 1 |  |  | 0 | bio-soluble fibres
 |  | MERV-15 | McMaster | 1mm | white | 1 |  |  | 1
Other

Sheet: FF Testing
Filtration Factor Testing. 60mL (BD Luer Lock) syringe, occluded on one end. Filter material tightly taped over open end with packing tape. Sampling line inserted through hole in sidewall of syringe
Machine - AccuFit 9000 (Levitt Safety)
Date: | 2020-05-05
Location: | Toronto General Hospital, Department of Anesthesia
Testers: | AS | WN
 | Filtration Factor (Outside particulate concentration : Inside particulate concentration, averaged by integral/time)
Run
1
2
3
4
5
6
7
Overall Filtration Factor | IGNORE | IGNORE | IGNORE | IGNORE | IGNORE | IGNORE | IGNORE | IGNORE | IGNORE | IGNORE | IGNORE | IGNORE
Average Filtration Factor | #DIV/0! | #DIV/0! | #DIV/0! | #DIV/0! | #DIV/0! | #DIV/0! | #DIV/0! | #DIV/0! | #DIV/0! | #DIV/0! | #DIV/0! | #DIV/0!
Note 1 - first 3 measurements used as equilibration time, and not included in average |  |  |  |  | Note 2
 |  |  |  |  | Overall Filtration Factor is given by a formula, where n= no. of runs, here n=7:
 |  |  |  |  | Overall FF = 1/(1/ff1 + 1/ff2 + 1/ff3 + 1/ff4 + 1/ff5 + 1/ff6 +1/ff7)

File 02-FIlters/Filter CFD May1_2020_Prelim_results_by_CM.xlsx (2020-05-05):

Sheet: Results
Preliminary flow testing
2020-05-01 |  | ambient air | Note: these results are only preliminary, and require verification before they should be applied.
Material |  | Blank |  |  |  | N95 |  |  |  |  | Bootie fabric
comment |  |  | repeat at end | average | av. diff. | meltblown dust mask | repeat at end | average | av. diff. | above blank | Single layer | above blank | Double layer | above blank | Halyard 100 | above blank | Halyard 400 | above blank | Halyard 600 | above blank | Halyard 650 | above blank | Containe | above blank | "Aerostar" | above blank | "Enduropleat" | above blank | RIDGID V56000 | above blank | Vestex | above blank
Q (SLPM) | Q/A (SLPM/m2) | DP (in. water) |  |  |  |  |  |  |  |  |  |  |  |  | no process |  | no process |  | no process |  | no process |  | no process |  | HVAC filter |  | HVAC filter |  | "Shopvac" HEPA filter |  | surgical mask fabric
0.5 | 17667.84452 | 0.1 | 0.1 | 0.1 | 0 | 0.2 | 0.15 | 0.175 | 0.025 | 0.075 | 0.1 | 0 | 0.1 | 0 | 0.15 | 0.05 | 0.15 | 0.05 | 0.2 | 0.1 | 0.15 | 0.05 | 0.7 | 0.6 | 0.1 | 0 | 0.1 | 0 | 0.6 | 0.5 | 0.1 | 0
1 | 35335.68905 | 0.1 | 0.15 | 0.125 | 0.025 | 0.2 | 0.2 | 0.2 | 0 | 0.075 | 0.1 | -0.025 | 0.1 | -0.025 | 0.4 | 0.275 | 0.6 | 0.475 | 0.6 | 0.475 | 0.6 | 0.475 | 1.9 | 1.775 | 0.15 | 0.025 | 0.1 | -0.025 | 1.6 | 1.475 | 0.15 | 0.025
1.5 | 53003.53357 | 0.1 | 0.15 | 0.125 | 0.025 | 0.2 | 0.25 | 0.225 | 0.025 | 0.1 | 0.1 | -0.025 | 0.15 | 0.025 | 0.65 | 0.525 | 0.95 | 0.825 | 1 | 0.875 | 1 | 0.875 | 4.25 | 4.125 | 0.2 | 0.075 | 0.15 | 0.025 | 3 | 2.875 | 0.2 | 0.075
2 | 70671.37809 | 0.1 | 0.15 | 0.125 | 0.025 | 0.3 | 0.35 | 0.325 | 0.025 | 0.2 | 0.2 | 0.075 | 0.2 | 0.075 | 1 | 0.875 | 1.5 | 1.375 | 1.4 | 1.275 | 1.4 | 1.275 | 5 | 4.875 | 0.2 | 0.075 | 0.2 | 0.075 | 5 | 4.875 | 0.35 | 0.225
2.5 | 88339.22261 | 0.1 | 0.15 | 0.125 | 0.025 | 0.4 | 0.45 | 0.425 | 0.025 | 0.3 | 0.25 | 0.125 | 0.25 | 0.125 | 1.3 | 1.175 | 1.85 | 1.725 | 1.8 | 1.675 | 1.8 | 1.675 |  |  | 0.3 | 0.175 | 0.25 | 0.125 |  |  | 0.5 | 0.375
3 | 106007.0671 | 0.15 | 0.2 | 0.175 | 0.025 | 0.4 | 0.55 | 0.475 | 0.075 | 0.3 | 0.3 | 0.125 | 0.3 | 0.125 | 1.6 | 1.425 | 2.2 | 2.025 | 2.3 | 2.125 | 2 | 1.825 |  |  | 0.35 | 0.175 | 0.3 | 0.125 |  |  | 0.65 | 0.475
3.5 | 123674.9117 | 0.15 | 0.2 | 0.175 | 0.025 | 0.5 | 0.65 | 0.575 | 0.075 | 0.4 | 0.35 | 0.175 | 0.4 | 0.225 | 1.8 | 1.625 | 2.65 | 2.475 | 2.75 | 2.575 | 2.4 | 2.225 |  |  | 0.4 | 0.225 | 0.35 | 0.175 |  |  | 0.8 | 0.625
4 | 141342.7562 | 0.2 | 0.2 | 0.2 | 0 | 0.6 | 0.8 | 0.7 | 0.1 | 0.5 | 0.4 | 0.2 | 0.45 | 0.25 | 2.1 | 1.9 | 3.2 | 3 | 3.2 | 3 | 2.9 | 2.7 |  |  | 0.5 | 0.3 | 0.45 | 0.25 |  |  | 1 | 0.8
4.5 | 159010.6007 | 0.25 | 0.25 | 0.25 | 0 | 0.7 | 0.95 | 0.825 | 0.125 | 0.575 | 0.5 | 0.25 | 0.5 | 0.25 | 2.4 | 2.15 | 3.8 | 3.55 | 4 | 3.75 | 3.4 | 3.15 |  |  | 0.6 | 0.35 | 0.5 | 0.25 |  |  | 1.2 | 0.95
5 | 176678.4452 | 0.3 | 0.3 | 0.3 | 0 | 0.8 | 1.05 | 0.925 | 0.125 | 0.625 | 0.6 | 0.3 | 0.6 | 0.3 | 2.8 | 2.5 | 4.5 | 4.2 | 4.75 | 4.45 | 4 | 3.7 |  |  | 0.65 | 0.35 | 0.6 | 0.3 |  |  | 1.55 | 1.25
5.5 | 194346.2898 | 0.35 | 0.3 | 0.325 | 0.025 | 1 | 1.25 | 1.125 | 0.125 | 0.8 | 0.75 | 0.425 | 0.75 | 0.425 | 3.2 | 2.875 | 5 | 4.675 | 5 | 4.675 | 4.75 | 4.425 |  |  | 0.8 | 0.475 | 0.7 | 0.375 |  |  | 2.3 | 1.975
6 | 212014.1343 | 0.4 | 0.4 | 0.4 | 0 | 1.1 | 1.4 | 1.25 | 0.15 | 0.85 | 0.85 | 0.45 | 0.8 | 0.4 | 3.6 |  |  |  |  |  | 5 | 4.6 |  |  | 0.9 | 0.5 | 0.75 | 0.35 |  |  | 2.8 | 2.4
6.5 | 229681.9788 | 0.4 | 0.4 | 0.4 | 0 | 1.2 | 1.5 | 1.35 | 0.15 | 0.95 | 0.95 | 0.55 | 0.95 | 0.55 | 3.9 |  |  |  |  |  |  |  |  |  | 1 | 0.6 | 0.85 | 0.45 |  |  | 3.4 | 3
7 | 247349.8233 | 0.5 | 0.45 | 0.475 | 0.025 | 1.3 | 1.75 | 1.525 | 0.225 | 1.05 | 1.05 | 0.575 | 1 | 0.525 | 4.3 |  |  |  |  |  |  |  |  |  | 1.1 | 0.625 | 0.95 | 0.475 |  |  | 4 | 3.525
 | averages |  |  |  | 0.01428571429 |  |  |  | 0.08928571429
 | 0.003 | radius
 | 2.827433388e-05 | area

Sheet: Materials
Material Mastersheet
Site | No. | Filter | Company | Thickness | Appearance | Plies in Pack | Origin | Cost | Woven | Comment | Web-Link
Lakehead |  | Bootie | Medi-Select | <1mm | Blue | 1 | China |  | 1 | Shoe-Cover Ref CCTS-R | www.medi-select.ca
 |  | MERV-8
 |  | MERV-8
Quang | Q-1 | Small vacuum bag | KEEPW6 | 1 | white | 3 | Amazon |  | 1 | 2 woven & 1 hepa filter
 | Q-2 | vacuum bag | VACURAMA | 1 | white | 3 | VACURAMA |  | 1 | 2 woven & 1 hepa Filter | vacurama.com
 | Q-3 | vacuum bag | VACURAMA | 2 | white | 4 | VACURAMA |  | 1 | 2 woven & 2 hepa filters | vacurama.com
 | Q-4 | surgimask | N/A | 1 | blue | 1 | Vietnam |  | 1 | surgimask
 | Q-5 | surgimask | N/A | 1 | blue | 1 | China |  | 1 | surgimask
UHN |  | H100 | Halyard | <1mm |  |  |  |  | 0
 |  | H300 | Halyard | <1mm |  |  |  |  | 0
 |  | H400 | Halyard | <1mm |  |  |  |  | 0
 |  | H600 | Halyard | <1mm |  |  |  |  | 0
UofT |  | MERV-14 | H&V | 2mm | clear-white | 1 |  |  | 0
 |  | Hepa Paper |  | <1mm | white |  |  |  | 0 | fibre-glass
Queen's |  | MERV-14 "Billings" | TBC | 2mm | green | 1 |  |  | 0 | bio-soluble fibres
 |  | MERV-15 | McMaster | 1mm | white | 1 |  |  | 1
Other

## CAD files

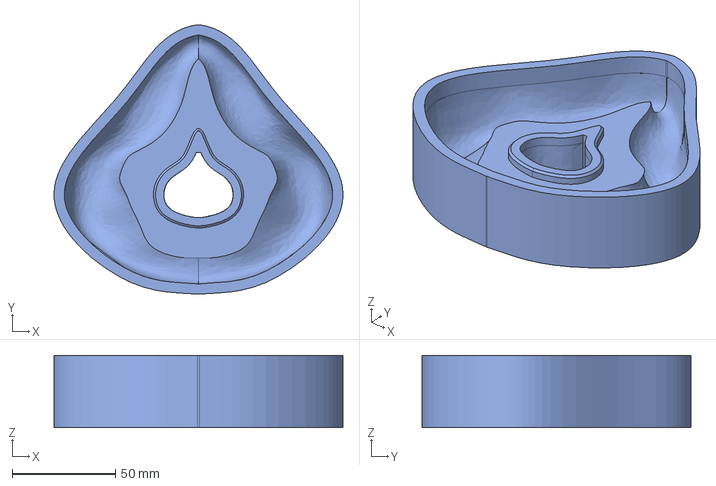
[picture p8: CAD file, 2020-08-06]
02-Design Types/Simple Silicone Mask "SSM"/Mask Mould/Duo 2020 July 21/Duo 7 Main - Mould part 1.step
140.1 x 130.6 x 35.0 mm

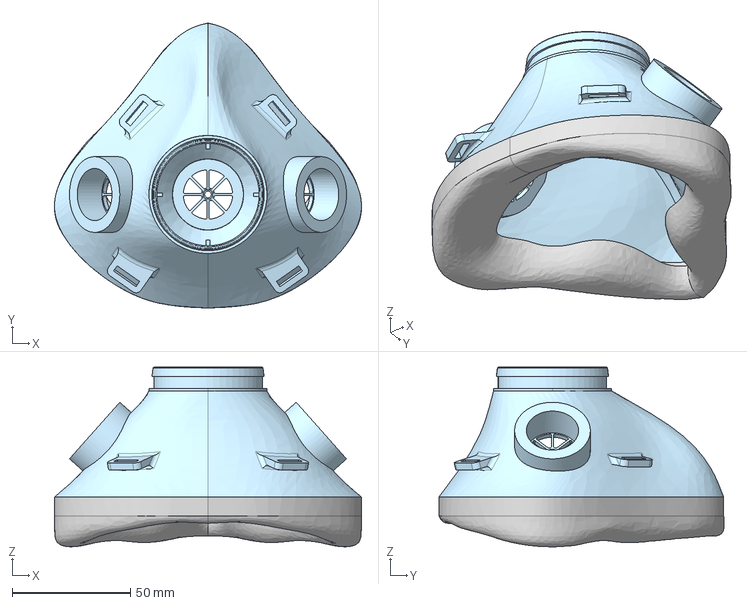
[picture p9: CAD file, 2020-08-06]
02-Design Types/Simple Silicone Mask "SSM"/Mask Mould/Duo 2020 July 8/Duo (June 19 interface - base) Main.step
130.1 x 120.8 x 76.1 mm

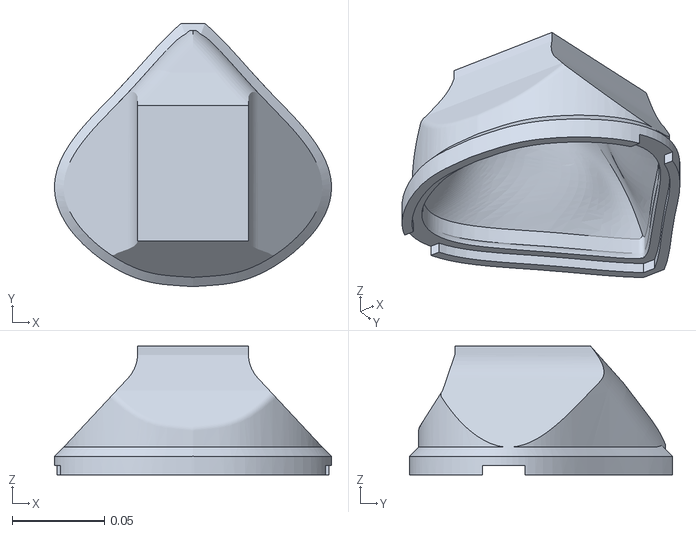
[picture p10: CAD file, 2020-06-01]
02-Design Types/Simple Silicone Mask "SSM"/Mask Mould/SSR Original 2020 Apr 12/Silicone mould assembly - Mould part 3.stl
0.15 x 0.143 x 0.0697

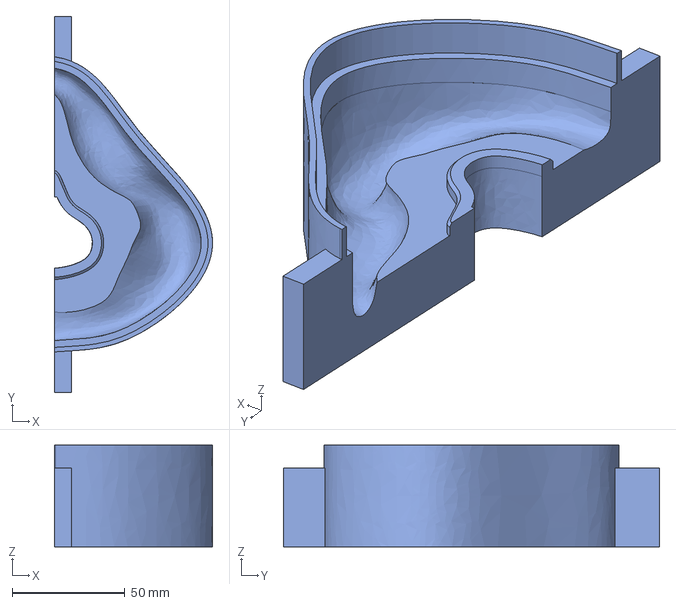
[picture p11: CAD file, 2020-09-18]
source files/3dprintablebodymask/cad/Duo 7 Main Clip [Aug 6 mod] - Mould part 1 - Right.step
70.0 x 166.6 x 45.0 mm

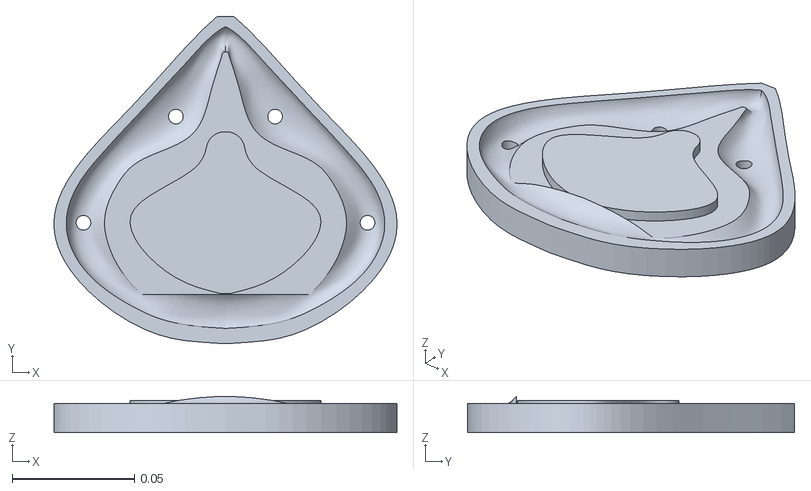
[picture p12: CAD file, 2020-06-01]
02-Design Types/Simple Silicone Mask "SSM"/Mask Mould/SSR Original 2020 Apr 12/Silicone mould assembly - Mould part 1.stl
0.14 x 0.134 x 0.0149

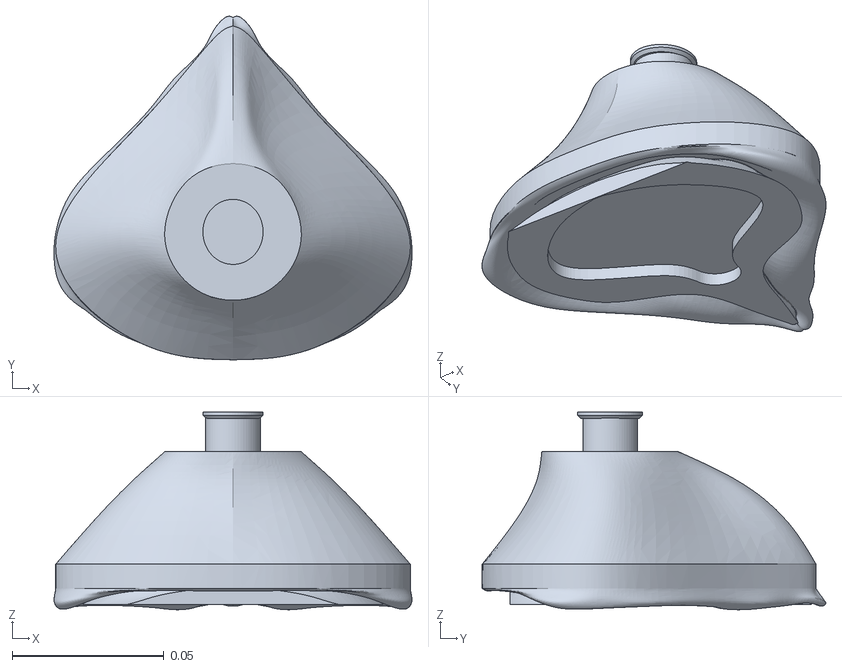
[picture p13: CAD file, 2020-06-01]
02-Design Types/Simple Silicone Mask "SSM"/Mask Mould/SSR Original 2020 Apr 12/Silicone mould assembly - Mould part 2.stl
0.118 x 0.113 x 0.065

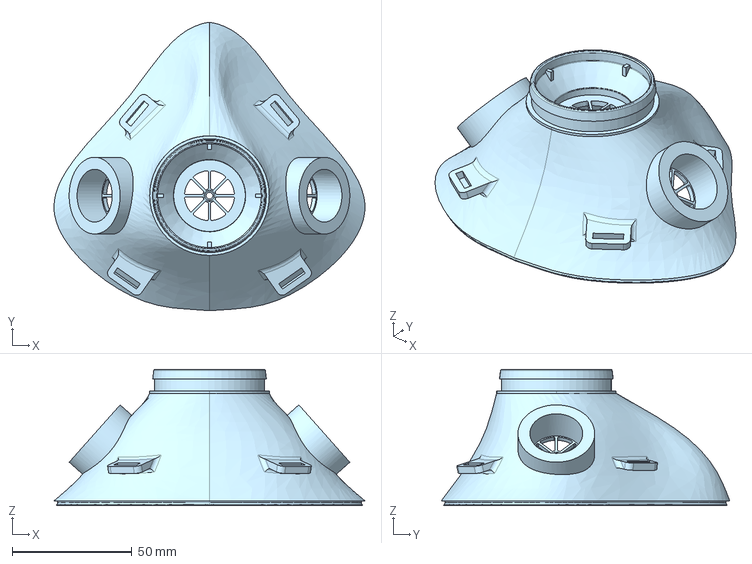
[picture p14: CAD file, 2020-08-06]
source files/3dprintablebodymask/cad/Duo 7 Main Body.step
130.1 x 120.6 x 57.0 mm

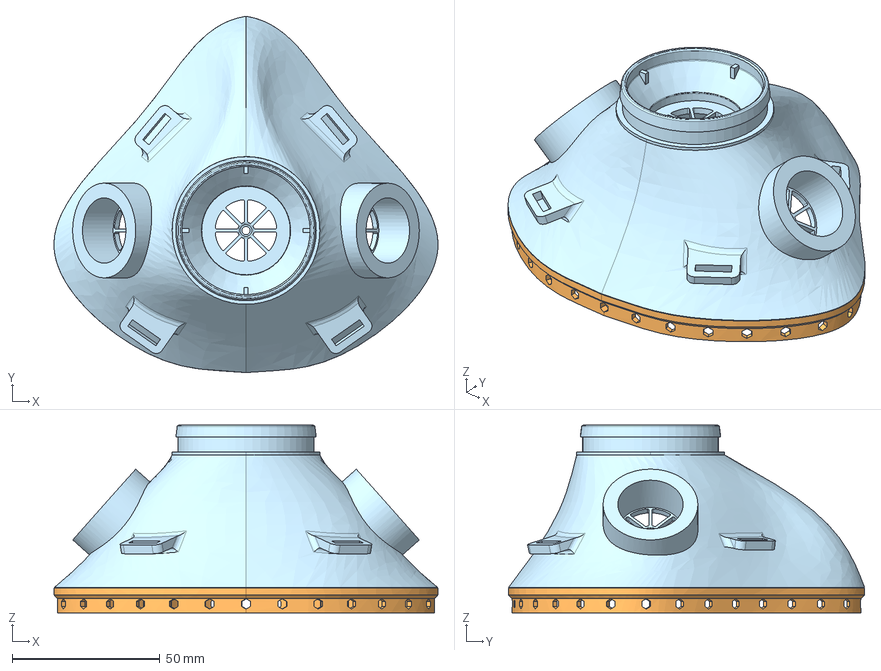
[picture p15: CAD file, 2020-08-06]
source files/3dprintablebodymask/cad/Duo 7 Main Clip.step
130.0 x 120.6 x 63.5 mm

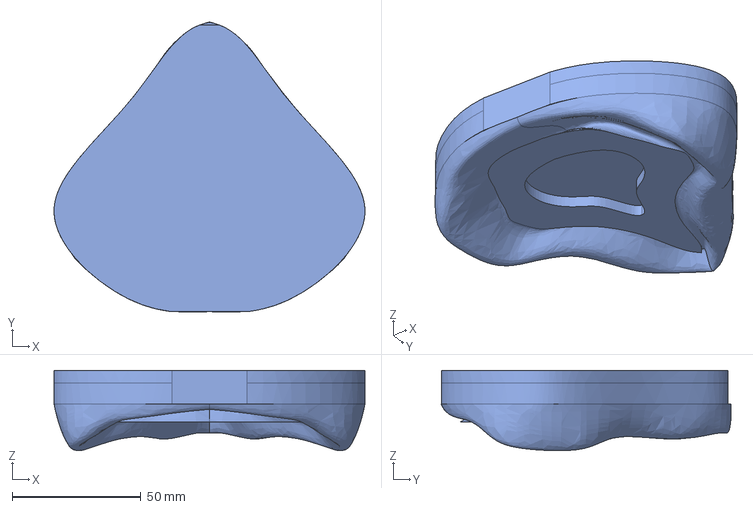
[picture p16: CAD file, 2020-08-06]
source files/3dprintablebodymask/cad/Duo 7 Main - Mould part 2.step
120.7 x 112.6 x 31.2 mm

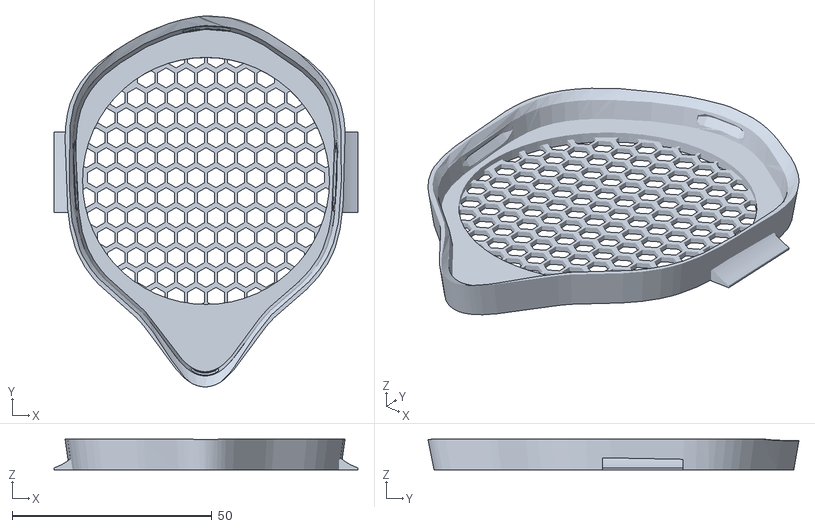
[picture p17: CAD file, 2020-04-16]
02-Design Types/3DP N95 Respirator Mask Design_1/Cartrige Version 3.stl
76.1 x 93.0 x 7.74

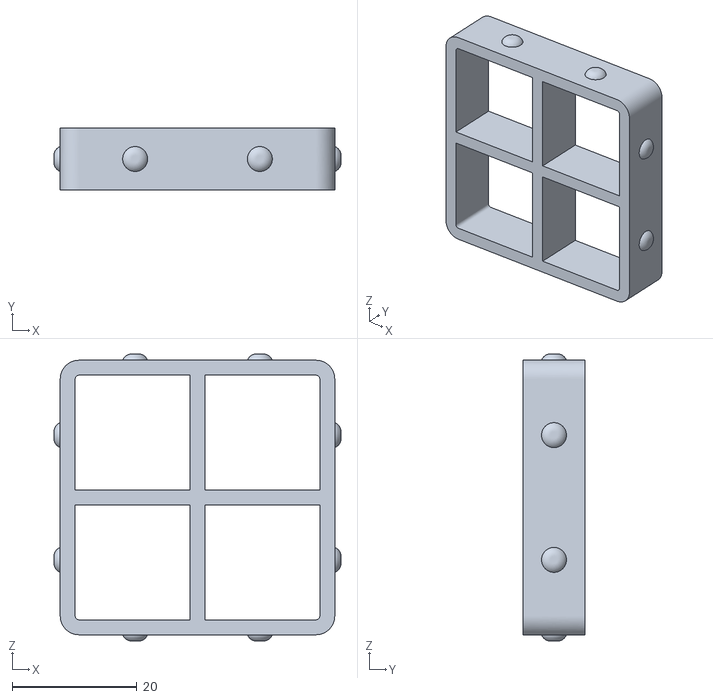
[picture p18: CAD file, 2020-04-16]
02-Design Types/Concordia 3D Mask Files/Concordia 3D Mask Files/mask filter.stl
46.0 x 10.0 x 46.0

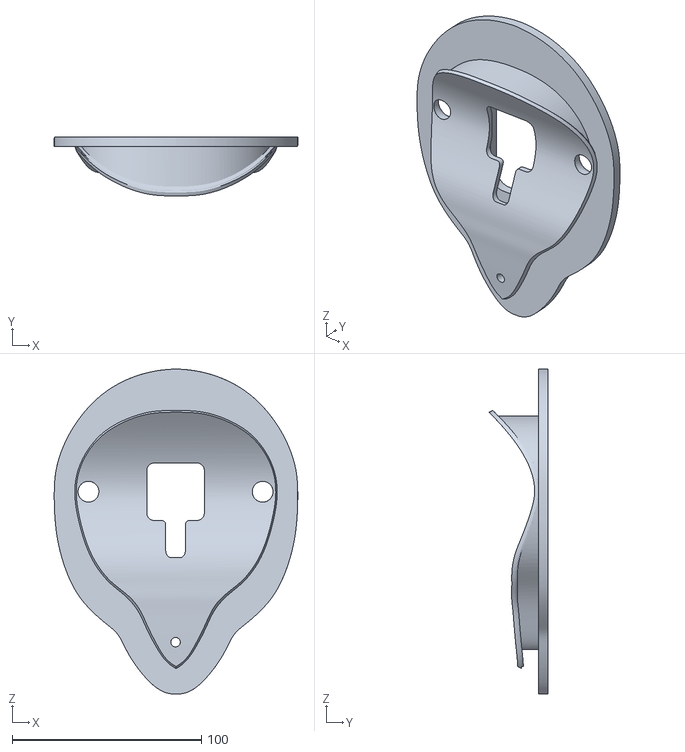
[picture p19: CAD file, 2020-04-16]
02-Design Types/Concordia 3D Mask Files/Concordia 3D Mask Files/Past Versions/4-6/mask mold lid.stl
128.5 x 31.1 x 171.5

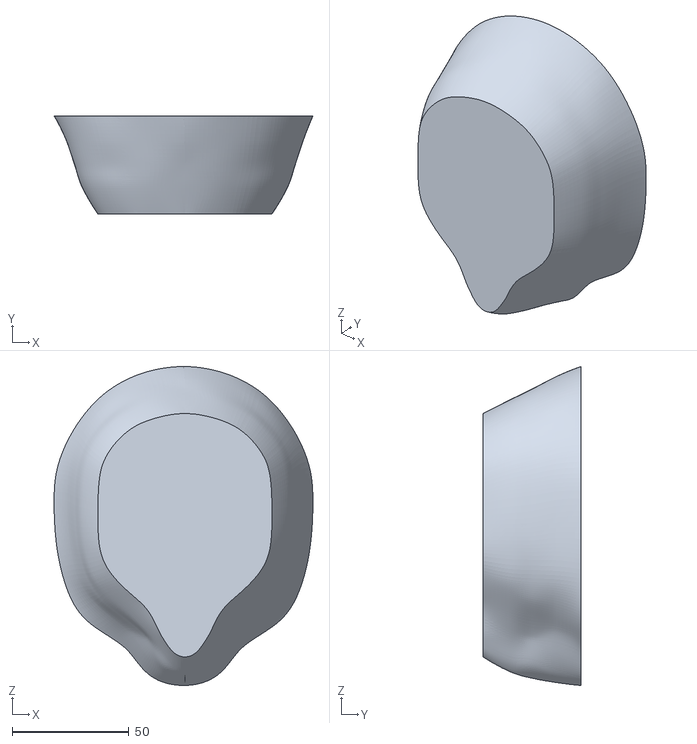
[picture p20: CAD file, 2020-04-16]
02-Design Types/Concordia 3D Mask Files/Concordia 3D Mask Files/Past Versions/4-8/mold bottom.stl
110.9 x 42.0 x 136.6

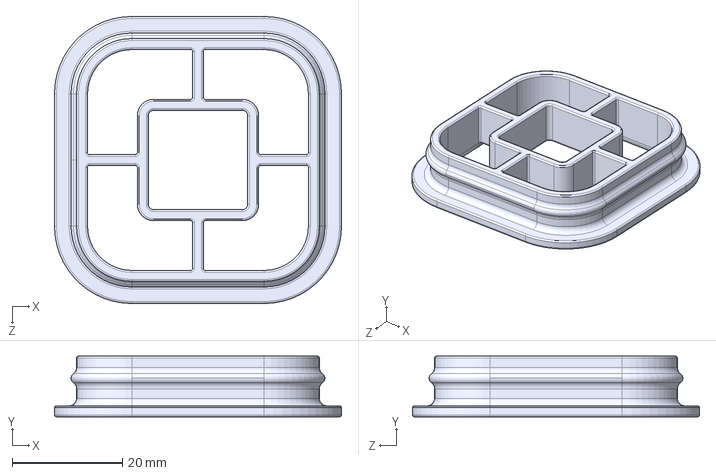
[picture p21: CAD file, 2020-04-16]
02-Design Types/I3D Modified Montana/I3D_Covid_FilterHolder_1_0gap_v4/I3D_Covid_FilterHolder_1_0gap_v4.STEP
52.0 x 11.0 x 52.0 mm

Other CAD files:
source files/3dprintablebodymask/cad/Duo 7 Main Clip [Aug 6 mod] - Mould part 1 - Left.step
02-Design Types/I3D Modified Montana/I3D_Covid_Mask_Medium_v4/I3D_Covid_Muzzle_Med.SLDPRT
02-Design Types/I3D Modified Montana/I3D_Covid_Mask_Small_v4/medium_lugs_v4.sldprt
02-Design Types/I3D Modified Montana/I3D_Covid_Mask_X_Small_v4/medium_lugs_v4.sldprt
02-Design Types/3DP N95 Respirator Mask Design_1/Filter Glasket.stl
02-Design Types/Archived Designs/3DP N95 Respirator Mask Design_1/Filter Glasket.stl
02-Design Types/Archived Designs/Concordia 3D Mask Files/Concordia 3D Mask Files/Past Versions/4-6/mask body.stl
02-Design Types/Archived Designs/Concordia 3D Mask Files/Concordia 3D Mask Files/Past Versions/4-6/mask mold base.stl
02-Design Types/Archived Designs/Concordia 3D Mask Files/Concordia 3D Mask Files/Past Versions/4-8/gasket.step
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

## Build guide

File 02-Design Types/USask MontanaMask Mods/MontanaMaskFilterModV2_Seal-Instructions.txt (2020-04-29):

MontanaMaskFilterModV2

Mask is intended to be used with soft silicone tubing (McMaster Products 5236k515 and 5236K507 or equivalent).
 An air-filled silicone ring is formed by cutting larger tubing to length, coating inside with silicone bonding agent, and slipping small section of smaller tubing inside joints of larger tubing. 
 Tubing is left to cure.

 Once ring is formed, it can be placed inside the seal channel of the mask. The ring is meant to be removable so that mask and ring can be properly cleaned in between uses.

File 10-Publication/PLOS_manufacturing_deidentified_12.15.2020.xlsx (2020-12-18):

Testing Information |  | Demographic Information |  |  |  |  |  |  |  |  | APIL SSM
Study ID | Date of Test (Month/Day/Year) | Age (Years) | Sex (M/F) | Height (cm) | Weight (kg) | BMI (kg/m^2) | Face Width (mm) | Face Length (mm) | NIOSH Panel | Naso-Menton Distance (mm) | Run #1 Normal Breathing | Run #2 Deep Breathing | Run #3 Head Side-to-Side | Run #4 Head Up-and-Down | Run #5 Talking out loud | Run #6 Bending over | Run #7 Normal Breathing | Overall Harmonic Fit Factor (Run 1-7) | Stationary Harmonic Fit Factor (Run 1,2,7) | Dynamic Harmonic Fit Factor (Run 3-6) | Pass/Fail (1,0) | Retest Y/N (1,0) | Mask Type | Mask Size | Filter Type
1 | 5/26/2020 | 33 | M | 186 | 85 | 24.57 | 135 | 127 | 7 | 102 | 196 | 118 | 93 | 127 | 83 | 92 | 104 | 108 | 129.35 | 96.28 | 0 | 0 | Manitoba SSR | M | Intersurgical Hydro-Mini
2 | 5/23/2020 | 40 | M | 169 | 53 | 18.56 | 132 | 118 | 3 | 92 | 362.97 | 273.41 | 579.62 | 272.93 | 218.76 | 292.98 | 343.75 | 308.44 | 321.83 | 299.10 | 1 | 0 | SSR MB-ON | S | DAR™ Mechanical Filter
3 | 5/23/2020 | 30 | M | 174 | 80 | 26.42 | 147 | 129 | 10 | 100 | 429.44 | 228.67 | 214.53 | 212.54 | 113.47 | 160.73 | 250.43 | 199.45 | 280.51 | 163.93 | 1 | 0 | SSR MB-ON | S | DAR™ Mechanical Filter
4 | 5/11/2020 | 42 | M | 180 | 98.9 | 30.52 | 135 | 132 | 9 | 110 | 17210.48 | 7457.45 | 53251.97 | 57043.76 | 1133.47 | 61842.89 | 99999999.99 | 6211.54 | 15608.07 | 4279.33 | 1 | 0 | SSM-D20 | M | AirGuard
5 | 5/7/2020 | 47 | M | 190.5 | 113.6 | 31.3 | 140 | 130 | 9 | 110 | 11144.24 | 7762.25 | 8716.52 | 7422.18 | 390.28 | 3130.88 | 8338.26 | 2017.53 | 8862.89 | 1277.50 | 1 | 0 | SSM-D20 | M | AirGuard
6 | 5/5/2020 | 44 | M | 172 | 75 | 25.35 | 132 | 126 | 7 | 120 | 99999999.99 | 10701.59 | 99999999.99 | 21075.01 | 2467.11 | 12724.02 | 18986.85 | 10332.02 | 20530.78 | 7527.52 | 1 | 0 | SSM-D20 | M | AirGuard
7 | 5/7/2020 | 62 | F | 171.5 | 71.4 | 24.28 | 121 | 125 | 6 | 100 | 99999999 | 25959.05 | 10240.16 | 16958.36 | 4234.82 | 2675.3 | 99999999.99 | 8694.65 | 77836.74 | 5218.18 | 1 | 0 | SSM-D20 | M | AirGuard
8 | 5/27/2020 | 34 | F | 157 | 59 | 23.94 | 149 | 115 | N/A | 108 | 1556 | 1536 | 1051 | 1621 | 1369 | 1321 | 994 | 1307 | 1304.49 | 1308.97 | 1 | 0 | SSM-D20 | M | AirGuard

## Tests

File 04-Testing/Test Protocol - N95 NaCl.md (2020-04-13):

Orig: Will Ng
Last: 2020-04-09

Time: 2020-04-13
Centre: Testing at UofT Occupational Safety and Environmental Health
Location: 223 College St., Toronto ON Canada M5T 1R4
Personnel: James Scott, Jeff Brook, Will Ng, Vahid Anwari, 1x Other
contact: 1.416.946.8778 james.scott@utoronto.ca

## Target
"System is dedicated to running the 30 L/min portion of the NIOSH 42 CFR Part 87 test for 
respiratory protection devices. It tests the devices against salt [NaCl] particles in the 
range of 10-400 nm. General purpose health care masks need to achieve 95% filtration efficiency 
based on overall particle counts." 

## Runs 1, 2, and 3

## Masks in order of preference 1 to 3, with fit testing on mannequin to confirm
### Montana Small Size or Medium Size
- Silicone rim
### NIH "SFM" Small Size Rev-A back-up
- Silicone rim
### NIH "SFM" Medium Size Rev-A back-up
- Silicone inlay
### I3D Small Size as back-up
- Window rubber seal
- Must be fully silicone-sealed by hand without gaps

## Filter Runs
1. N95 3M 5N11 no sandwich
2. Woodbridge INAOC Filter (prepackaged layer = 5 ply), sandwiched by Halyard H100 x 2 ply
3. Roxon RX1568 spirometry filter (purple) with adapter on Montana Mask or I3D Mask (we have both)
4. Halyard H300 x 2 ply without filter within

## To Do: 10 April - 12 April 2020 [Easter Friday to Sunday]
Investigate how Montana mask people have "sewn" the 2 pys of Halyard together [Matt]

Make filters and "sew" edges for NIH cartridge. [Vahid]

Make straps suitable for NIH small mask. [Vahid]

Make silicone fit-seal for NIH. [Josh and Thomas]

Make Adapter for NIH and I3D. [Josh]

___

Alternative testing centres: 
- SickKids Hospital. Dr. Maynes' Lab (Portacount): jason.maynes@sickkids.ca
- Ontario Power Generation X Labs, through Dr. Mukesh Bhargava: mbhargava@nhh.ca
-- best to have a point of contact for OPG's covid-19 response

___

To Do: Decontamination testing next. Viral testing design. Need to investigate.

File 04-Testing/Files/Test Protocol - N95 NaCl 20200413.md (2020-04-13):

Orig: Will Ng
Last: 2020-04-09

Time: 2020-04-13
Centre: Testing at UofT Occupational Safety and Environmental Health
Location: 223 College St., Toronto ON Canada M5T 1R4
Personnel: James Scott, Jeff Brook, Will Ng, Vahid Anwari, 1x Other
contact: 1.416.946.8778 james.scott@utoronto.ca
Attendees: Andrew, Vahid, Will, Matt

## Target
"System is dedicated to running the 30 L/min portion of the NIOSH 42 CFR Part 87 test for 
respiratory protection devices. It tests the devices against salt [NaCl] particles in the 
range of 10-400 nm. General purpose health care masks need to achieve 95% filtration efficiency based on overall particle counts." 

## Runs 1, 2, and 3

## Select Mask - in order of preference 1 to 5, with fit testing on mannequin to confirm
1. NIH "SFM" Small Size Rev-A
- Silicone rim (EcoFlex 30)
2. NIH "SFM" Medium Size Rev-A
- Slicone rim (EcoFlex 30 Dragon Skin 10 blend), or
- Silicone inlay (Dragon Skin 10)
3. Montana Small Size
- Silicone rim (EcoFlex 30)
4. Montana Medium Size
- Silicone rim (EcoFlex 30)
5. I3D Small Size as back-up
- Window rubber seal with silicone inner seal

## Once a Mask and size is determined, then we run the same mask for 3 different filters
## Filter Runs - in order of preference 1 to 4,
1. N95 3M 5N11 no sandwich
2. Woodbridge INAOC Filter (prepackaged layer = 5 ply, we have option to take away plies)
3. Roxon RX1568 spirometry filter (purple) with adapter on NIH, Montana Mask, or I3D Mask
4. Halyard H400 x 2 ply without filter within

## Video tape and take notes of problems

## Also send results to CIGITI, Queen's

## To Do: 10 April - 12 April 2020 [Easter Friday to Sunday]
- Investigate how Montana mask people have "sewn" the 2 pys of Halyard together [Matt]

- Make filters and "sew" edges for NIH cartridge. [Vahid]

- Make straps suitable for NIH small mask. [Vahid]

- Make silicone fit-seal for NIH. [Josh and Thomas]

- Make Adapter for NIH and I3D. [Josh]

___

Alternative testing centres: 
- SickKids Hospital. Dr. Maynes' Lab (Portacount): jason.maynes@sickkids.ca
- Ontario Power Generation X Labs, through Dr. Mukesh Bhargava: mbhargava@nhh.ca

___

To Do: Decontamination testing next. Viral testing design. Need to investigate.

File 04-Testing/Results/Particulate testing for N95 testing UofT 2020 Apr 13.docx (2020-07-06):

N95 Replacement Proof of Concept Testing. Location: Gage building UofT, Dala Lana School of Public Health.

APIL Lab Team: William Ng, Andrew Syrett, Vahid Anwari. Note: These preliminary test results are for internal use only, not meant to be conclusive evidence, but for proof of concept testing or official results.

| Parameter Resistance (Inches H2O). | Expected | Total particles passing through #/cm^3 | Flow | Material | Conclusion
1st seal test room air -Entire mask sealed with aluminum tape | -5.3 | - 1000 or infinitely negative | 12x10^3 (Ideal: <20) | 30 L/min | NIH medium mask, Dragon skin 30 (blue) silicon, Filter material: 2 ply N95 filter (56 mm x 56 mm | Leakage + smaller particles passing through at high velocity due to low surface area
2nd seal test room air. Mask sealed except at area of filter | -3.98 | Same as above | Similar to above | 30 L/min | Same as above | Same as above
3rd seal test - entire surface area sealed with aluminum tape | -9.94 | Same as above | Similar to above | 30 L/min | NIH medium mask, Dragon skin 30 (blue) silicon, Filter material: 3 ply N95 filter (56 mm x 56 mm
Matt’s mask around mannequin head – Sealed with aluminum tape | - -17 | Same as above | ≈ 270 | 30 L/min | Sewn Halyard 400 | Better than above – higher surface area. Still suffers from leakage at sewn area of the head bands on each side. Has potential, improve with heat treated seams, and retest.
Roxon – attached to hose | -3.96 | Same as above | | 30 L/min | Lots of leakage, low resistance | Low surface area, not enough filter material
Woodbridge 5 ply Taped over mouth of mannequin with aluminum tape | -14.6 | Same as above | 142 (Reference <20 ideal). Best N95 = 0 particles with perfect seal. Median sized particle: 50 nm | 30 L/min | Woodbridge 5 ply. Velocity of particles near mask = 0.2 m/s | Low surface area, inconclusive.
N95 filter (3 ply) roughly < 1.5”x1.5” attached to mannequin head with aluminum tape | -9.2 | Same as above | 173, median size 76 nm | Flow 30L/min | 3M 5N11 N95, 3 ply. | Low surface area reduces filter effectiveness at high flow rates of 30 L/min

Overall Conclusions: Problems with leakage with the NIH model despite thorough taping with aluminum tape. The 5.7 cm x 5.7 cm filter area reduces surface area during inspiration, allowing smaller particles with higher velocities to pass through even the 3 ply N95. Nylon cage of the NIH mask does not stick well to the aluminum tape and makes it difficult to seal. The mannequin head is not to proportion compared to an ideal facial shape. Significant leakage issues and the low surface area for filtering in NIH model and the “montana” and its derivative models renders these designs non testable for NIOSH level testing with NaCl.

Future directions: Increased SURFACE AREA of filter area is mandatory – particles detectable by the test was 10 nm – 500 nm. Good level filters prevent the passing of particles >20 nm, 3M N95 masks with excellent seal perform with 0 particles passing through, has high surface area.

Nylon filament and other 3D printed masks not recommended due to poor sealing and very low surface area.

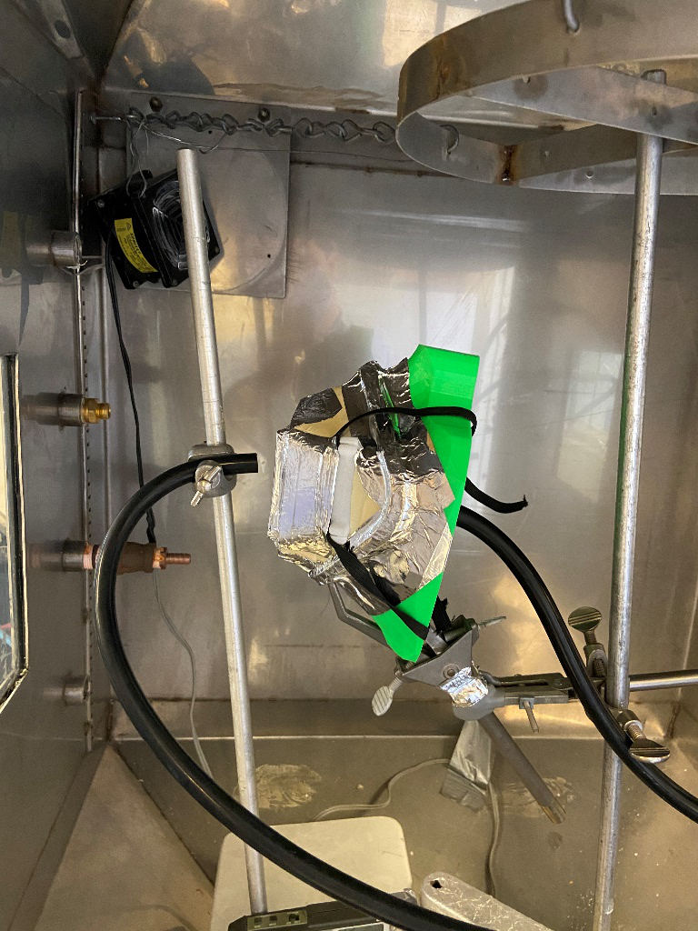
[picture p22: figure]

| NIH medium mask, Dragon skin 30 (blue) silicon, Filter material: 3 ply N95 filter (56 mm x 56 mm

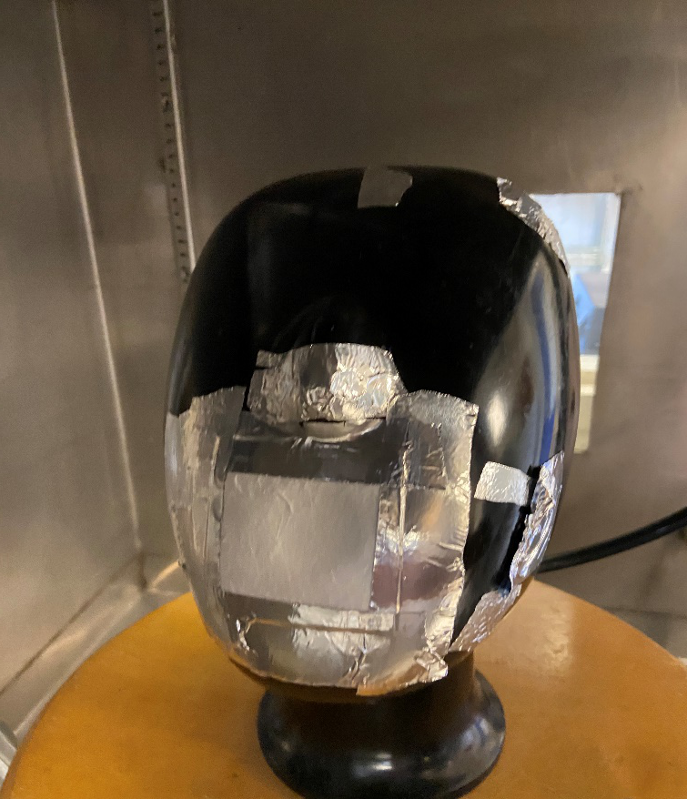
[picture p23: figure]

| Woodbridge filter taped with aluminum tape over mannequin head testing resistance

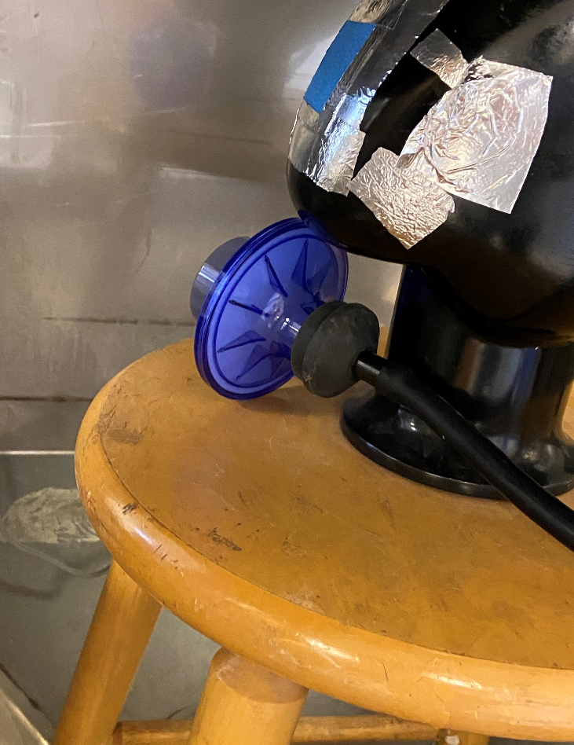
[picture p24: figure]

| Resistance testing the Roxon filter

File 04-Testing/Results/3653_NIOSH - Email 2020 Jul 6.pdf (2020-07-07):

Monday, July 6, 2020 at 15:26:14 Atlan5c Daylight Time

Page 1 of 2

Subject: [External] Re: Question: Filter testing report JOB NUMBER: 3653-001 Date: Monday, July 6, 2020AD at 12:59:49 Atlantic Daylight Time
From: Bruce Urch
To: | Ng, William, Aerosol Testing DLSPH
CC: | Anwari, Vahid, Mary Speck, Jessica Trac, James ScoW

William,

1) The pressure drop for filter/mask test #1 was -21.3 mm H2O or -0.84 inches H2O.
2) With lab air the count inside the mask was 16.8 particles/cc.
2) With salt the average count inside the mask was 2,143 particles/cc.
3) The FE formulae is 100 x [(outside - inside) / outside].
For the mass FE we use the sum of the particle volume x counts for the 54 particle sizes from 10.4 to 469.8 nm diameter midpoint.

Bruce

From: Ng, William <William.Ng@uhn.ca>
Sent: July 2, 2020 7:16 PM
To: Aerosol Testing DLSPH <aerosol.testing.dlsph@utoronto.ca>; Bruce Urch <bruce.urch@utoronto.ca> Cc: Anwari, Vahid <vahid.anwari@uhn.ca>; Mary Speck <m.rutherford@utoronto.ca>; Jessica Trac <jessica.trac@mail.utoronto.ca>
Subject: Question: Filter testing report JOB NUMBER: 3653-001

Dear Bruce and Mary

Thanks to you both for all the hard work and resources.

Vahid and I just wanted to ask Bruce 3 things:
1. Did we have a seal pressure measured for the face-piece with the filter? And did it measure < -1000 in.
| water as expected?
2. With the raw particle count, the expected count number is <20 / cm^3, what was the actual particle
| count for this (FE-99.7%),
3. by what number do we divide the particle count to get the actual %? I forgot what you once told me.

Thank you for the pressure drop measurement, that is reassuring.

Truly,

William C. K. Ng
MBBS MMed FANZCA FRCPC
Anesthesia and Pain Management, Toronto General Hospital
TGH Research Institute & UHN Advanced Perioperative Imaging Lab (PI) Pediatric Cardiac Anesthesia, SickKids Hospital
Faculty Dept. of Anesthesiology, University of Toronto

M 1.857.330.7399

Page 2 of 2

P 1.416.714.1973

Soli Deo Gloria

From: Aerosol Testing DLSPH <aerosol.testing.dlsph@utoronto.ca> Date: Tuesday, June 23, 2020AD at 14:08
To: "Ng, William" <William.Ng@uhn.ca>
Cc: James ScoW <james.scoW@utoronto.ca>
Su
2) bject: [External] Filter testing report

Hi William,

AWached are the results of our testing of the filter media you provided.

Please sign and return a copy of the aWached agreement leWer.

Best Regards,

Aerosol Testing Laboratory
Dalla Lana School of Public Health Gage Bldg, Room 302
223 College, Toronto, Ontario M5T 1R4
aerosol.testing.dlsph@utoronto.ca

This e-mail may contain confidential and/or privileged information for the sole use of the intended recipient.
Any review or distribution by anyone other than the person for whom it was originally intended is strictly prohibited. If you have received this e-mail in error, please contact the sender and delete all copies.
Opinions, conclusions or other information contained in this e-mail may not be that of the organization.

If you feel you have received an email from UHN of a commercial nature and would like to be removed from the sender's mailing list please do one of the following:
(1) Follow any unsubscribe process the sender has included in their email
(2) Where no unsubscribe process has been included, reply to the sender and type "unsubscribe" in the subject line. If you require additional information please go to our UHN NewsleWers and Mailing Lists page.
Please note that we are unable to automatically unsubscribe individuals from all UHN mailing lists.

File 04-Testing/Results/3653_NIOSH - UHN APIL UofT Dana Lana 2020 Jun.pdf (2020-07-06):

FILTRATION EFFICIENCY REPORT SUMMARY | JOB NUMBER: 3653-001
Attn: | Dr. William Ng, UHN, Toronto
From: | Dr. James Scott, Division of Occupational & Environmental Health, DLSPH, U of Toronto
Method: | MODIFIED NIOSH 42 CFR Part 84 (30 L/min)
No. of tests: | 2
Report date: | 2020-06-19

RESULTS SUMMARY
SAMPLE # | DESCRIPTION | * FEmass(%)
1
† | Air Guard Clear – attached to face piece | 99.7
2 | Hydro Guard Mini – filter only | 99.9

NOTES: *Filtration efficiency calculated as a function of particle mass

†Pressure drop: -21.3 mm H2O

DESCRIPTION OF PROCEDURE
Masks were subjected to a modified NIOSH 42 CFR Part 84 test regimen. In brief, filtration efficiency was measured under conditions of unidirectional airflow at 30 L/min through masks fitted to a test mannequin and exposed in an atmosphere of salt aerosol of median diameter ~80 nm. Particles were measured by size category using a TSI SMPS model 3034 and expressed as counts or mass (standard protocol assesses filtration efficiency by mass).

DISCLAIMER
The Governing Council of the University of Toronto and the author(s) of this Report expressly disclaim any warranty, expressed or implied, that this Report or any information in connection therewith, including but not limited to warranties on design, performance, and materials described herein, meet the requirements of any laws, rules, standards, or governmental specifications; and use or reliance on this Report for any purpose is entirely the responsibility of the user of this Report. This Report is not to be reproduced without permission and is for use only of its intended recipients who commissioned it

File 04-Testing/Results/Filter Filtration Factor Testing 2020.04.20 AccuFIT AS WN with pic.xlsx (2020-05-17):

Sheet: Filtration Factors
Filtration Factor Testing. 60mL (BD Luer Lock) syringe, occluded on one end. Filter material tightly taped over open end with packing tape. Sampling line inserted through hole in sidewall of syringe
Machine - AccuFit 9000 (Levitt Safety)
Date: | April 20 2020
Location: | Toronto General Hospital, Department of Anesthesia |  |  |  |  |  |  |  |  |  |  |  | 4/26/2020 Additional Filters |  |  | 2020-05-01
Testers: | AS | WN
 | Filtration Factor (Outside particulate concentration : Inside particulate concentration, averaged by integral/time)
Run | N95 NIOSH Moldex | Camfil Vacuum Filter MERV15 1 ply | Camfil Vacuum Filter MERV15 2 ply | Woodbridge 5 Ply | Halyard H400 2Ply | Halyard H100 2Ply | NIOSH 5N11 | NIOSH 5N11 Repeat | Billings MERV14 1 Layer | Billings MERV14 2 Layer | HV MERV 14 1 ply | MERV14 with H100 1 Layer | HVMerv14 1-ply | HVMerv14 2-ply | HVMerv14 1-ply & H100 1-ply | Blue Shop Towel
1 | 143 | 52.9 | 428.2 | 29.52 | 16.51 | 5.78 | 13.06 | 7431.23 | 15 | 432.02 | 31.08 | 77.85 | 22.9 | 273.5 | 85.15
2 | 171 | 55.17 | 553.35 | 96.77 | 28.04 | 9.44 | 70.95 | 1794.58 | 44.61 | 495.42 | 43.68 | 105.32 | 25.5 | 304 | 84.4
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

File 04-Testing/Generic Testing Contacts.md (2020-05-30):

Orig: Andrew Syrett
Last: 29 May 2020, Will Ng
Title: Testing Contact List

Upload as Markdown: Will

# Commercial Equipment incl. ASTM
- [Nelson Labs, Utah](https://www.nelsonlabs.com/)
- [Cambridge Testing, Missasauga](http://www.cambridgematerials.com/)
- [Element (Material and Mechanical Testing)](https://www.element.com/locations/the-americas/burlington)
- [NTS Automotive Testing](https://www.nts.com/location/kitchener-ontario/) (incl. biological, need mroe details)

# Particulate Filtration Testing

1. James Scott Lab – James Scott, Jeff Brook, Bruce Urch.  Division of Occupational & Environmental Health.  
-	Phone: 416-946-8778
-	Email: james.scott@utoronto.ca
-	Email: jeff.brook@utoronto.ca

# QNFT (quantitative) Mask Fit Testing

## Internal Contacts
1. UHN OCC Health and Safety – Craig Parsons (TGH Safety Manager)
-	via Will, email craig.parsons@uhn.ca
2. SickKids facility – Jason Maynes (or his technician)
-	Email Will Ng or Devin Singh (Apr-May 2020)
-	via Will, email Eric Greenwood: eric.greenwood@sickkids.ca
-	via Will, email Jason Maynes: jason.maynes@sickkids.ca

3. Will Ng/David Clinkard – both trained on PortaCount

## External Contacts
4. Levitt-Safety – commercial fit testing company.
-	Email: gail.macpherson@levitt-safety.com

# QLFT (qualitative) Mask Fit Testing (Bitrex)
1. TGH (TBC)

2. Queen’s team (via Royal Military College, Dr. Dixon) – Via Leah Allen
- Email: lallen@qmed.ca

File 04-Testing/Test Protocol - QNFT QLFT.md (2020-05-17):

Orig: Will Ng

Last: 2020-05-12

# QNFT 
## Ambient Aerosol Count Ratio "Fit-Factor"
- "A Fit Factor is a number that is the direct result of a quantitative respirator fit test. It is a measurement made by an instrument during a simulation of workplace activities (the exercises). It is expressed as the challenge aerosol concentration outside the respirator divided by the challenge aerosol concentration that leaks inside the respirator DURING A FIT TEST"
- [TSI definition summary](https://www.tsi.com/getmedia/f07681c1-a465-40d0-9add-85cc5813f0ad/Fit-Factors-vs-Protection-Factors-App-Note-(ITI-023)-US?ext=.pdf)
- TSI PortaCount (r) or Levitt-Safety AccuFIT (r)
- https://en.wikipedia.org/wiki/Respirator_fit_test#Quantitative

## NIOSH US BiVariate Facial type
- https://www.cdc.gov/niosh/npptl/resources/pressrel/letters/conformityinterp/CA-2019-1011.html
- Andrew: "the total number needed is 18.  See the table in the attached document.  This is the minimum number so long as you meet the number required according to the population distribution."
- technically 2 donnings per mask type.

## Continuous Negative Pressure "Air Leak Test"
- Quantifit 3000 from OHD
- https://ohdusa.com/

## APF
- APF 10 for N95
- "An Assigned Protection Factor is the level of protection that a particular type of respirator can be expected to provide 95% of the time. An APF of 10 means that type of respirator (if used properly) can be safely used in an atmosphere that has a hazardous concentration of up to 10 times the Permissible Exposure Limit (PEL) for that hazard. APF's are determined by the government or a standards organization. In the United States, the National Institute of Occupational Safety and Health (NIOSH) and the American National Standards Institute (ANSI) both establish APF's for various types of respirators. For example, a half face negative pressure air purifying respirator typically has an APF of 10. Most full face negative pressure air purifying respirators typically have an APF of 50." quote from [TSI PDF](https://www.tsi.com/getmedia/f07681c1-a465-40d0-9add-85cc5813f0ad/Fit-Factors-vs-Protection-Factors-App-Note-(ITI-023)-US?ext=.pdf)

# QLFT
## Bitrex testing "spray-under-hood" with UHN OHS or UofT OSEH
- Date TBC
- Location TBC

# ASTM Testing
## Interteks
- ~ $2000 to $3000 (per Leah Allen, Queen's May 2020)
- BFE, PFE, Fluid Resistance, Flame Spread, Delta P (breathability)

## Surgical Mask
### Breathability
- FT2100 standard

___

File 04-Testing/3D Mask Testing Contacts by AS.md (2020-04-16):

Orig: Andrew Syrett
Last: 15 April 2020, Will Ng
Upload as Markdown: Will

Particulate Filtration Testing

1.	 James Scott Lab – James Scott, Jeff Brook, Bruce Urch.  Division of Occupational & Environmental Health.  
a.	Phone: 416-946-8778
b.	Email: james.scott@utoronto.ca
c.	Email: jeff.brook@utoronto.ca

QNFT (quantitative) Mask Fit Testing

Internal Contacts
1.	UHN OCC Health and Safety – Craig Parsons (TGH Safety Manager)
a.	via Will, email craig.parsons@uhn.ca
2.	SickKids facility – Jason Maynes (or his technician)
a.	Email Will Ng or Devin Singh (Apr-May 2020)
b.	via Will, email Eric Greenwood: eric.greenwood@sickkids.ca
c.	via Will, email Jason Maynes: jason.maynes@sickkids.ca

3.	Will Ng/David Clinkard – both trained on PortaCount

External Contacts
4.	Levitt-Safety – commercial fit testing company.
a.	Email: gail.macpherson@levitt-safety.com

Qualitative (QLFT) Mask Fit Testing (Bitrex)

1.	Queen’s team (via Royal Military College, Dr. Dixon) – Via Leah Allen
a.	Email: lallen@qmed.ca

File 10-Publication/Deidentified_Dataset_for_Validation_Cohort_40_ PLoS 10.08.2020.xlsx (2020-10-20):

Study Identification |  | Demographic Information |  |  |  |  |  |  |  |  | Bitrex tested 3M N95 |  |  |  |  |  |  |  |  |  |  |  |  |  | APIL SSM |  |  |  |  |  |  |  |  |  |  |  |  |  |  | Feedback
Study ID | Date of Test (yyyy/mm/dd) | Age (Years) | Sex (M/F) | Height (cm) | Weight (kg) | BMI (kg/m^2) | Face Width (mm) | Face Length (mm) | NIOSH Panel | Naso-Menton Distance (mm) | 3M Model | Negative Pressure Test | Run #1 Normal Breathing | Run #2 Deep Breathing | Run #3 Head Side-to-Side | Run #4 Head Up-and-Down | Run #5 Talking out loud | Run #6 Bending over | Run #7 Normal Breathing | Overall Harmonic Fit Factor (Run 1-7) | Stationary Harmonic Fit Factor (Run 1,2,7) | Dynamic Harmonic Fit Factor (Run 3-6) | Pass/Fail (1,0) | Retest Y/N (1,0) | Run #1 Normal Breathing | Run #2 Deep Breathing | Run #3 Head Side-to-Side | Run #4 Head Up-and-Down | Run #5 Talking out loud | Run #6 Bending over | Run #7 Normal Breathing | Overall Harmonic Fit Factor (Run 1-7) | Stationary Harmonic Fit Factor (Run 1,2,7) | Dynamic Harmonic Fit Factor (Run 3-6) | Pass/Fail (1,0) | Retest Y/N (1,0) | Mask Type | Mask Size | Filter Type | Comfort (0-5) | Ease of Breathing (0-5)
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

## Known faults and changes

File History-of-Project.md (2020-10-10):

Orig: [William Ng et al.](www.anesthesia.utoronto.ca/faculty/william-ck-ng)

Project: Reusable N95 Respirator, aka "RNR", aka "Reusable N95 Stop-Gap" in the time of respiratory viral pandemic

Note: The SSM and SSM Duo reusable N95 respirator are experimental medical devices that have been subject validated in 40 and 42 volunteers at a single institution and are intended for pandemic disaster use after firstline disposable N95 respirators; they have not been endorsed by the originating health institution.

Last: 6 Jul 2020

Read: [Article on Medium](https://medium.com/@williamckng/stop-gap-n95-mask-in-the-time-of-covid-19-a615be38eb31?sk=8cc15ac6d79773021198b74c7c400207)

# Reusable-N95-StopGap-Project
## [APIL](https://apil.ca)-[CIGITI](https://www.cigiti.ca)-[GLIA](https://glia.org)-[Lakehead](https://northernontarioppe.ca)-McMaster-NOSM-[Queen's](http://ppekingston.squarespace.com/)-USASK-[UofT](https://www.3dppegtha.ca) collab
### Urgent design, testing, recommendation, upscale, dissemination of stop-gap N95 mask options with guidelines in light of disrupted N95 supply to COVID-19 era Canada
- This collaborative is an open-source, data-sharing, parallel development of the common goal (see CERN 2.0 License)
- Investigate back-up stop-gap plan for N95 depletion in Ontario, Canada, [see Article on Medium.com](https://medium.com/@williamckng/stop-gap-n95-mask-in-the-time-of-covid-19-a615be38eb31)
- Reuse of disposable N95 is preferred at this stage by decontamination (VPHP, UVGI, Heat).

## CAD Repo
- github [~/Design Types](https://github.com/tgh-apil/Reusable-N95-Project/blob/master/02-Design%20Types/Types%20List.md), or
- dropbox repo (and other big files, please ask [William Ng](mailto:william.ng@uhn.ca))

## [Mattermost](group.emlondon.ca)
- Team chat channel, email [William Ng](mailto:william.ng@uhn.ca)

## [Project Timeline](https://github.com/tgh-apil/Reusable-N95-Project/blob/master/00-Timeline/Timeline%20Projection%20N95.md)

*Current focus*
- form-fit test Simple Silicone Mask "SSM" c. InterSurgical AirGuard | Hydro-Mini ~HME~ HEPA filters: test & refine
- ~form-fit test APIL NIH Unibody Silicone Respirator with HME bacterial/viral filters~ pause on this design
- UHN PPE committee review of SSM as part of 3M N95 conservation strategy

*Weekly focus*
- HC MDEL (Nasa, Arash, Vahid, Will, Dorotea from GLIA)
- Modified NIOSH at Gage (week of 25 May 2020)
- SSM Duo prototype with insp. and exp. silicone valves, +/- TAVISH valves from Sameeer
- Volunteer testing: *SSM + AirGuard pass rate >99%, 3M N95 <75%, n=44* 
- Aim 5 iterations max for every 104 volunteers. (Will et al.)
- TME Inc. with 2nd stop-gap for testing (pass rate >90%)
- Funding (OCE vetting done, proposal due 11 Jun 2020, MITACS, NRC)
- 1st paper on Conception and Production of SSM (Vahid/Arnaud), 2nd paper on Subject Validation of SSM as "Reusable N95 StopGap" (Andrew/Will)

*Filter Challenge*
- 2nd Leap (pre-clinical trial phase *now*): SSM Duo with dual OTS pleated HEPA filters, one-way valves to preserve filters, improve breathing and audio quality 
- Then followed by alternative filter material, tightly-sealed cartridge system to increased surface area for airflow. (Lakehead-NOSM Team Andre, Chris, Mike, Siamak; UofT R&D Team Arash, Chandra, Jessica, Nasa, Natasha, Yu; also thanks Jake Bender from GLIA for [bayonet designs](https://www.thingiverse.com/thing:4302122))
- Bayonet adapter prototype test 3M 2000 and 6000X series
- 3rd Leap: Complete filter replacement solution.

*Medium term challenge*
- Send samples to partners (lakehead, queen's, others who enquire)
- Funding
- Multi-site testing for reproducibility and validation: *on hold*.
- Reduce silicone load of SSM by 25% and reduce production time and labour
- Industry partner(s) to produce own mask body and/or disseminate SSM and upscale option(s).
- Medical Grade filter sourcing, preferred non-HME as they produce condensation on wearer-side (DAR, Intersurgical)
- Comparative estimation of *Benefit*, *Cost* and *Time* to producing first 1000 units.
- Set-up rolling working group Jun 2020 ff
- *Pandemic Resurgence Jun 2020 - Aug 2020 ff*

## [Design Options](https://github.com/tgh-apil/Reusable-N95-Project/tree/master/02-Design%20Types)
### SSM (UHN APIL and CIGITI)
- Derived from SSR, new geometry, new mould, new process.
- Modular adapters that can fit anything to silicone seal.
- SSM S - 90% downsize (73% by volume); will need 95% (86% by volume)
- New prototype "Dual Port" with 3 modular adapters for 2 filters and 1 exp. valve or 1 filter and 2 exp. valves, or other combo
### Toronto MicroElectronics
- Plastic with dual-collar silicone rim
### NIH released open sources
- https://3dprint.nih.gov/collections/covid-19-response
- many variations to choose from, apart form the above, which have gained traction and use in several hospitals
- UHN APIL modification to Unibody Silicone with *adapter for 15mm to 22mm adapter* (TBC).
### Simple Silicone Respirator (MB-ON collab)
- created by Christian Petropolis (Plastics Surgery) at HSC Manitoba; [UHN APIL refining, validating, developing](https://github.com/tgh-apil/Reusable-N95-Project/tree/master/02-Design%20Types/SSR%20MB-ON) 
- silicone material dragon skin sx pro to 10, durometer 2A - 10A
- attaches to commerical filters 15mm to 22mm; M size fits small to large; planning for S and L sizes.
- [original cad](https://cad.onshape.com/documents/912751c654360860ae260334/w/75644efc74b9616c5ac20c2f/e/7fecc2776bb556dd9c7c6a62), [Christian's Github](https://github.com/cpetropolis/Simple-Silicone-Respirator)
### ["Kingston" Mask - Queen's Initiative](http://ppekingston.squarespace.com/)
- Modification of Montana with different sizing, filter size, geometry, *nose-pinching mechanism*
- working in parallel with USASK on sealing with silicone rims to flexible PLA/TPU mask bodies
- fit-testing done by OSH at KGH
### [USASK Mask](https://medicine.usask.ca/news/2020/usask-engineering-team-designing-3d-printed-n95-masks-to-help-combat-covid-19.php)
- Flexible TPU with silicone ring applied to mask-rim, *large* mask filter casing
### Montana 3D by Billings, Montana
- website: Instagram #MakeTheMask, https://www.makethemasks.com
### Intermountain 3D (I3D) modification of Montana
- website: https://www.intermountain3d.com/covid-respirators.html
### Concordia (Wisconsin) masks
- https://blog.cuw.edu/COVIDmasks/, both modification of Montana and dual-cartridge, folded 3DP models.

## Prototype, Refinement [(Natasha, Jess, Andy, et al.)](#APILUHN)
- SSM ~Manitoba SSR~ M (S done) - 8 May 2020
- *SSM Dual Port M - prototype required 20 May 2020*
- Seal and fit problem - seal adequate 24 April 2020, comfort and breathabilith (nasal pad adjustment)
- Onepiece Silicone Iteration - required 24 April 2020 - done
- Filtration area needs to be maximally increased for WOB and any remote chance of getting NIOSH testing
- Considering 2 filter cartridge system with tight seal (Lakehead|Andre, APIL|UofT R&D, NOSM|Michael, Jay Pooley)
- Montana S, M, L size (modified) - (CIGITI|Brandon)
- Kingston XS, S, M, L, XL, Snowcone S, M - Fit-test Kingston Masks from Queen's - 23 April 2020
- ~NIH S, M. (XS needs redesigning)~ - pause on this 15 April 2020
- ~I3D XS, S, M prototypes built~ - archived
- ~Adapter to ROXON filter functional as stop-gap option~ (no longer pursued given poor NIOSH testing)
- ~single filter cartridge system with N95 medium~ (no longer pursued given poor breathability with good mask seal)

## [Local Testing](https://github.com/tgh-apil/Reusable-N95-Project/tree/master/04-Testing) [(Will et al.)](#UofT)
### Particulate and NIOSH test
- 104 feasible for 4-5 iterations of publishable volunteer data
- James Scott and Jeff Brook from UofT OS & EH 13 April 2020 - proof of concept testing
- excluded single FLAT N95 filter option, either double cartridge system, or pleated bacterial/viral filter required.
- Consider pursuing N90 grade with Merv 15 filter (suggested by Queen's https://www.mcmaster.com/22905k28)

### [OSHA and Bitrex Testing](https://github.com/tgh-apil/Reusable-N95-Project/blob/master/04-Testing/Test%20Protocol%20-%20Bitrex.md)
- Portacount or AccuFIT fit-testing as per OSHA/CSA protocol, standard 7 Fit-Factor Rubric: https://www.osha.gov/laws-regs/regulations/standardnumber/1910/1910.134AppA
- Pooling Non-UHN partners SickKids, Queen's University (KHSC), other OHS to perform CSA standard mask-fit test
- Functional Test as for any in-person testing using "spray under the hood" Bitrex
- UHN OHS involved, Craig Parsons and Sharon Martin (Mgr Frank Turner). UHN IPAC represented by Dr Alon Vaisman.

### Other centres through [Health Canada](https://www.canada.ca/en/health-canada/services/drugs-health-products/medical-devices/covid-19-unconventional-manufacturing-personal-protective-equipment.html)
- https://www.intertek.com/canada/ (https://www.intertek.com/scientific-regulatory-consultancy/)
- https://gcttg.com/en/ (textiles transportation geosynthetics)
- http://www.cambridgematerials.com (raw materials)

## [Decontamination](https://github.com/tgh-apil/Reusable-N95-Project/blob/master/06-Decontamination/Decontamination%20Protocol.md) [(Vahid)](#APILUHN)
- Designs ideally be washable in chlorox 1:10 (as for faceshields) and dried
- Will eventually need microbiology to chip in
- Viral testing is a possibility

## [Production](03-Production) (Vahid)
- TBC: APIL, UofT AScE|MD Team, GLIA
- Mould (Industry)
- Silicone vs. Rubber (Industry)
- Straps (Vahid)
- Filter Material, Seams (Yu, Chandra, Matt)
- Filter Adapter and Encasing (TME, UofT R&D)

## [Regulation and Standards](https://github.com/tgh-apil/Reusable-N95-Project/blob/master/05-Regulation/Regulatory%20List.md) (Nasa, Arash)
### Health Canada
- [HC MDEL](https://www.canada.ca/en/health-canada/services/drugs-health-products/medical-devices/covid19-personal-protective-equipment.html#a2), and 
- [HC COVID-19 PPE](https://www.canada.ca/en/health-canada/services/drugs-health-products/medical-devices/covid19-personal-protective-equipment.html)
### ISO and CSA 
- CSA Z94.4/18 for respirator fitting

## Budget
### Capital outlay
### Cost per unit
### Labour
### Dissemination and Delivery
- UHN|APIL
- 3D GTHA
- PPE Kingston
- Partners

## Funding
### Ontario Together initiative to help fight COVID-19, 
- submitted: 12:30pm, 9 April 2020 by Will; responded to Ministry invitation, 18:15 17 April 2020.
- margaret.kinyanjui@uhnresearch.ca with internal template and actual application
### NSERC
- submitted: 25 April 2020 by Will
### FastFund
- submitted: 12 April 2020 by Carla
### CIHR
- submitted: 12 May 2020 by Will
### MITACS
### OCE
### NRC
### Other Sources
- see contacts list
- ~UHN Peter Munk Innovation Fund: due 20 Apr 2020~ (Cardiovascular Focus)
### Community
- Li Zhang (GLIA volunteer) to raise awareness and medium-term community funding

## Long Term
### Patent final product/s report
### Non-Pandemic Use recommendations
### Model refinement dependent on on-going funding
### Publish then archived for future pandemic back-up response use

## Team
### UofT
- [William Ng](www.anesthesia.utoronto.ca/faculty/william-ck-ng) (Lead, Anesthesia, Principal Investigator @ UHN|APIL)
- [Azad Mashari](www.anesthesia.utoronto.ca/content/azad-mashari) (Director of UHN APIL, Anesthesia)
- [Andrew Syrett](doctors.cpso.on.ca/DoctorDetails/Syrett-Andrew-James/0295170-103261) (Writer, Anesthesia, Testing)
- [Arnaud Mbadjeu](www.anesthesia.utoronto.ca/sites/default/files/tgh_fellows_photos_jan_2020.pdf)
- [Matt Ratto](https://ischool.utoronto.ca/profile/matt-ratto/) (TEDA Director)
- [Eric Greenwood](www.anesthesia.utoronto.ca/content/eric-greenwood) (SickKids Advisor, Director of Equipment)
- [Devin Singh]() (Filtration, Testing, Engineering|Anesthesia)
- [James Scott](www.dlsph.utoronto.ca/faculty-profile/scott-james-a/) (OS & EH)
- Alon Vaisman (UHN IPAC physician, UHN COVID-19 PPE team, UofT Infectious Diseases)
- Dmitry Rozenberg (UHN Advisor, Respirology and Lung Transplant)
- [Binu Jacobs](www.linkedin.com/in/binu-jacob-98b53a95/) (Senior Research Scientist)
### APIL|UHN
- UHN Advanced Perioperative Imaging Lab (https://apil.ca)
- [Joshua Hiansen (Design Engineering, Print Lead)]
- [Vahid Anwari (Production, Biomedical Engineer)](www.linkedin.com/in/vahid-anwari-3763973)
### UofT School of Applied Science & Engineering
- [Nasa Nguyen](https://www.linkedin.com/in/nasanguyen/) (Project Manager), [email](mailto:nasa.nguyen@mail.utoronto.ca)
- [Natasha Valenton](https://www.linkedin.com/in/natasha-valenton/) (R&D Lead: Fusion, CAD)
- [Arash Nourimand](https://www.linkedin.com/in/arash-nourimand/) (PR Lead, industry funding)
### Data Team
- [Maggie Ziao]() (UAlberta MD, R data science)
- [Vince Nguyen]() (St Louis MD, Toronto MicroElectronics Partner, dataviz and message)
### UofT MD Program | Hamilton SoM ["3D-PPE-GTHA"](https://www.3dppegtha.ca) 
- Student Body, Community Presence, Logistics
- [Jessica Trac](https://www.linkedin.com/in/jessica-trac/) (R&D Team Coordinator)
- [Andy Afenu](https://www.linkedin.com/in/andy-edem-afenu-72048597/) (R&D Team)
- [Sinthu Senthillmohan](https://www.linkedin.com/in/sinthu-senthillmohan/) (Communications) 
- [Yousuf Ahmed](https://www.linkedin.com/in/yousufahmed4/) (Communications)
### UofT TEDA
- [Yu Zou](https://www.linkedin.com/in/zouyubob/) (UofT MSE, Polymer Printing)
- [Chandra Singh]() (UofT MSE|MIE, Fluid Dynamics Engineering)
### UHN Kotra Group | UofT Krembil Research
- [Lakshmi Kotra](https://pharmacy.utoronto.ca/faculty/lakshmi-kotra) (Viral RT-PCR)
### CIGITI, SickKids - https://www.cigiti.ca
- [Thomas Looi (Director)](https://www.linkedin.com/in/thomas-looi-ba657a8/)
- [Brandon Peel (Design)](https://www.linkedin.com/in/brandonpeel/)
### Lakehead|[NOSM's Parallel Initiative](https://northernontarioppe.ca/) 
- Andre LaFreniere (Engineering, Lakehead)
- Chris Murray (Engineering, Lakehead)
- Siamak Elyasi (Engineering, Lakehead)
- Michael Poling (3D print, face-shields, NOSM Faculty, Division of Clinical Sciences)
- Alannah MaClean (Student Lead, NOSM)
### McMaster University
- Clinical Leads: Suneel Upadhye and Rahim Valani
- Victoria McKinnon (MD Program, Inksmith)
- Samveg Shah (MD Program, Engineering)
- Lawrence Porter (Sheridan College, School of Engineering)
- (Andrew Syrett moving to McMaster, St Joseph's Hospital in July 2020)
### [Queen's Parallel Initiative](http://ppekingston.squarespace.com/) (SoM)
- Cesia Quintero & Megan Singh & Matt Snow (Founders)
- Taylor Sweet (YGK 3D, co-designer)
### USASK's Engineering Team - google drive tbc
- Grant Tingstad (Engineer)
- Erik Olson (Engineer)
### Key Community Partners
- Andrew Pho ([Lancotek](https://lancotek.com), manager)
- James Garel Jones ([VertiGrow](https://vertigrow.io), Queen's co-designer)
- Quang Nguyen, CEO [247 Security](https://www.247securityinc.com), CEO [TME inc](http://tme-inc.com)
- Steve Cory ([Objex Unlimited](https://objexunlimited.com/), CEO)
### GLIA NFP partner - https://glia.org
- Carrie Wakem (Executive Director)
- Dorotea Gucciardo (HC MDEL)
- Jessica and Andrew Schroeder (Mattermost, R&D)
- Jake Bender (LHSC)
- ~Seeking joint grant proposal for Peter Munk Innovation Fund (Aim for 19 April 2020)~ (CV focus)
#### EM|UHN
- Sameer Masood (Emergency Physician, UHN and Humber)
- Expiratory TAVISH-like valve with filter
- Aim to share filtering knowledge, testing results, combine human factors simulation.
### SickKids Research
- Jason Maynes, SickKids Research Chair (Portacount lab), viral testing lab (TBC)

### Affiliates and Contacts
#### UHN Vascular Surgery "Development of a non-disposable N95" - UHN AMO grant
- [Graham Roche-Nagle, Vascular Surgery, partner Panon Plastics](https://surgery.utoronto.ca/content/graham-roche-nagle)
#### Dr. Nanthakumar from TGH Cardiology 
- offering 3DP machines' spare capacity and engineering help
- Stephane Masse (3DP Engineer)
#### [Manitoba Health Sciences Centre](https://github.com/cpetropolis/Simple-Silicone-Respirator)
- Christian Petropolis (3DP Mask Lead, Plastics Surgery)
- SSR had HC approval 19 May, 2020. We agreed to be their Ontario Partner April 2020.
#### NHH (Northumberland Hills Hospital)
- Mukesh Bhargava (Director)
#### Other Industry
- Rick Struthers (True North PP, owner)
- Lucia Iannantuono (McMaster Engineering, TN 3S)
- Brian Read (ex-plastcs; industry co-ordinator) 
#### Woodbridge indsutry, CEO Bob Magee
- VP (NVH) Martin Mazza - Technical POC regarding filter

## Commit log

2020-04-04 Add files via upload
    Health Canada 20200331 statement on 3D printed devices
2020-04-04 Add files via upload
    HC statement 20200331 on standards fo 3D printing
2020-04-05 Add files via upload
    Chlorine Dioxide & VPHP and Decontamination Chamber.
2020-04-07 Update Parts List
    listed parts of first prototype 5 April 2020
2020-04-07 Add files via upload
    Prototype parts
2020-04-10 Add files via upload
    2020-04-09
    Dear Dr. Ng:
    The Mask parts are donated by: Richard Smeenk, Agile Manufacturing, Inc. (Agile) at the request of Brian Read. The masks are known as Stopgap Face Mask (SFM) by the National Institute of Health (NIH):
    This device is intended to be use only for the duration of the public health emergency related to COVID-19. The decision to implement this device should be made with careful consideration and under t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
    The Stopgap Face Mask was designed to be a surgical mask intended to provide liquid barrier protection for medical purposes… This mask sho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
2020-04-10 Delete Health Canada 20200331 3D Printing and Manufacturing.pdf
    moved to Regulations
2020-04-13 Protocol and Roxon
    Protocol 20200413
    ROXON filter part RX1463, 1465, 1466
    But no RX1568
2020-04-13 RX1568 product RX1467
    https://roxon.ca/en/product/rx1568-viral-bacterial-filter/#1569460361195-8e0ee081-45f0
2020-04-13 Testing Results template
    new add NaCl NIOSH result template
    [NaCl NIOSH Test Results 13 Apr 2020 WNg et al.xlsx]
2020-04-13 Update NaCl NIOSH Test Results 13 Apr 2020 WNg et al.xlsx
    [NaCl NIOSH Test Results 13 Apr 2020 WNg et al.xlsx]
2020-04-13 Update NaCl NIOSH Test Results 13 Apr 2020 WNg et al.xlsx
    actual runs planned
    [NaCl NIOSH Test Results 13 Apr 2020 WNg et al.xlsx]
2020-04-13 test results uploaded
    Particulate Testing at James Scott Lab 2020-04-13
    [Copy of N95 Project Management will-edits.xlsx, N95 Project Management will-edits.xlsx]
2020-04-14 Timeline Update
    New Tasks
    Old Tasks crossed
    Manitoba vs. NIH
    [Copy of N95 Project Management will-edits.xlsx, Raw Proof of Concept TestApril 13 2020 tests 2-5.xlsx]
2020-04-14 Timeline Update
    Colour-code status boxes
    [Copy of N95 Project Management will-edits.xlsx]
2020-04-14 Timeline renamed
    [N95 Project Management 20200413.xlsx, Old - N95 Project Management will-edits.xlsx]
2020-04-14 OSHA upload
    https://www.osha.gov/laws-regs/regulations/standardnumber/1910/1910.134AppA
    [NaCl NIOSH Test Results 13 Apr 2020 WNg et al.xlsx]
2020-04-14 Update README.md
    added current focus
2020-04-16 mask types uploaded individually
    [Cartrige Version 3.stl, Commercial filter example.iges, Commercial filter example.step, Facemask_Simple_Large_MF_REV2.STL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]
2020-04-17 STL CAD files
    [Medium NIH mask open Filter.STL, Normal Filter with handles.STL, Open Filter with handles.STL, Small NIH mask open Filter.STL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]
2020-04-18 upload SSR stuff
    [Medium harness - Part 1.stl, Posterior harness (prototype) - Part 1.stl, Silicone strap mould - Part 1.stl, Strap locks (prototype) - Part 1.stl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]
2020-04-21 Filtration Factor Testing 20200420
    AS and WN
    [Filter Filtration Factor Testing 2020.04.20 AccuFIT AS WN with pic.xlsx, NaCl NIOSH Test Results 13 Apr 2020 WNg et al.xlsx]
2020-04-21 Update Filter Filtration Factor Testing 2020.04.20 AccuFIT AS WN with pic.xlsx
    [Filter Filtration Factor Testing 2020.04.20 AccuFIT AS WN with pic.xlsx]
2020-04-23 testing files
    [Filter Filtration Factor Testing 2020.04.20 AccuFIT AS WN with pic.xlsx, Raw Proof of Concept TestApril 13 2020 tests 2-5.xlsx]
2020-04-23 SSR Manitoba
    Major update with .step files.
    [Commercial filter example.iges, Commercial filter example.step, Medium harness - Flat Mould v1.stl, Medium harness.step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]
2020-04-23 Kingston Tests
    2020-04-22
    [Kingston Snowcone N95 Mask QNFT Fit Testing 2020.04.22.xlsx]
2020-04-23 bender plugs
    bayonet style plugs for 3M firefighting mask.
    [maleBayonetFCV1.FCStd, maleBayonetFCV1.stl]
2020-04-24 Arash's Harness uploaded
    for manitoba mask
    [Mark-Harness-v3 .step, Mark-Harness-v3.sldprt]
2020-04-25 design types
    organised folder
    [Cartrige Version 3.stl, Filter Frame - Universal.stl, Filter Glasket.stl, Filter.stl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]
2020-04-25 Strap Moulds
    Natasha's striaght strap moulds 46 and 50 cm.
    [Silicone Strap Mould V2 460mm.stp, Silicone Strap Mould V3 500mm.stp]
2020-04-26 Testing 2020-04-25
    Manitoba 2 complete runs
    [Kingston Snowcone N95 Mask QNFT Fit Testing 2020-04-22.xlsx, Manitoba N95 Mask V1 Fit Testing 2020-04-25.xlsx]
2020-04-26 moving nanohack folder
    [v10.2_disc.stl, v10.2_gyroiddisk.stl, v10.2_lock.stl]
2020-04-27 UofT ON Manitoba revisions
    Major revisions.
    Folder Name change to SSR MB ON
    [Commercial filter example.iges, Commercial filter example.step, Mark-Harness-v3 .step, Mark-Harness-v3.sldprt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]
2020-04-27 Fit Test Template
    FIt Test 2020-04-26 and Fit Test Template for Volunteer testing.
    [Manitoba N95 Mask V2 and Filter Testing 2020.04.26 AccuFIT WN.xlsx]
2020-04-27 Testing Template File
    Testing Template .xlsx
    [Filter Filtration Factor Testing 2020.04.20 AccuFIT AS WN with pic.xlsx, MB-ON N95 Mask Testing Template 2020.04.27 AccuFIT WN.xlsx]
2020-04-29 Design Folder
    Adding USASK designs - flexible TPU, silicone ring seal.
    [MontanaMaskFilterModV2 v2.step, MontanaMaskPlugV2.stl]
2020-05-01 Design JB upload
    [Adapter Female v001.ipt, Adapter Female v002.ipt, Adapter Female v003.ipt, Adapter Male v002.ipt]
2020-05-02 Prelim Testing CFD
    prelim testing CFD on filter materials.
    [May1_2020_Prelim_results_by_CM.xlsx]
2020-05-03 Pleated Filter Cartridge Ref
    study from taiwan 2008
2020-05-04 Test Results updated
    CM results
    [Filter CFD May1_2020_Prelim_results_by_CM.xlsx]
2020-05-04 Move design folder type
    FCV by Bender
    [Commercial filter example.iges, Commercial filter example.step, Mark-Harness-v3 .step, Mark-Harness-v3.sldprt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]
2020-05-05 Filter folder
    new filter focus, mastersheet of types fo materials
    [Filter CFD May1_2020_Prelim_results_by_CM.xlsx, Filter Materials 202005.xlsx]
2020-05-17 Tavish, Testing, Results, Filters
    [Filter Filtration Factor Testing 2020.04.20 AccuFIT AS WN with pic.xlsx, Filter Materials 202005.xlsx, Raw Proof of Concept Test 13 Apr 2020 tests 2-5.xlsx, ta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]
2020-05-22 Data Visual
    One Page Infographic 2020-05-20
    [Filter Material 2020-05-16 parsed.xlsx]
2020-05-27 SSM Budget
    Budget for UHN 2020-05-25
    [Reusable N95 Cost Benefit Projection 2020-05-25 WNg.xlsx]
2020-05-30 Update Filter Materials List.md
    Filter List labelled and added
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2020-06-01 Mould Update on github
    Update and tidy up mask mould folder
    [Dual Port 2 - Mould Part 3 - Left.stl, Dual Port 2 - Mould Part 3 - Right.stl, Dual Port 3 - Mould Part 3-Open cap-Left.stl, Dual Port 3 - Mould Part 3-Open ca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]
2020-06-01 strap folder
    update and tidy up strap folder
    [Mark-Harness-v3 .step, Mark-Harness-v3.sldprt, Mask-Harness-Duo-(M)-V5.stl, Mask-Harness-Duo-(M)-v2.step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]
2020-06-01 Adapters - Valves
    Update and TIdy up adapters and valves
    [3M Adapter - Clear Valve.stl, 3M Adapter - Yellow Valve.stl, 3M Adapter - seat V1.stl, Cartridge Base (1).stl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]
2020-06-01 Harness Folder
    Tidy Up
    [Mask-Harness-Duo-(M)-v3.stl, Mask-Harness-Duo-(M)-v4.stl]
2020-06-01 Valves
    Medical Grade Silicone
    [PRT0006_220520.STEP, PRT0007_220520.STEP]
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2020-07-06 Design and References
    Adding Bayonet and lots of References.
    [3M-6200-Exhalation-Filter-Cover-FINAL.stl, 3M-6200-Exhalation-Filter-Holder-FINAL.stl, 3M-7500-Exhalational-Filter-Holder-Final.stl, 3M-Bayonet-to-15mm-Adapter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]
2020-08-06 Duo Jul 2020
    new versions Duo Jul 2020
    [3mm thick mask - interface mod - Mould part 1.step, 3mm thick mask - interface mod - Mould part 3 - L v1.stl, 3mm thick mask - interface mod - Mould part 3 - L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]
2020-08-06 renaming mask mould subfolders
    subfolders to include years, add "SSR" to original subfolder
    [Mask Mould part 1 and 2 - Mould part 1 - Modified 0.5mm.step, Medium silicone mask - Silicone mask (step 1).step, SSM 3mm thick mask - interface mod - Mould pa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]
2020-08-06 moving files
    moving valve-adapter files to new folder
    [Exp Valve Adapter C18.stl, Exp Valve Adapter C26.5 v2.stl, Exp Valve Adapter C26.5 v3 - no cylinder - rectangle tabs.stl, Exp Valve Adapter C26.5 v3 rectangle 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]
2020-09-18 added latest version files
    [3mm thick mask - interface mod - Mould part 1.step, 3mm thick mask - interface mod - Mould part 3 - L v1.stl, 3mm thick mask - interface mod - Mould part 3 - R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]
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2020-10-20 de-identified data SSM 40 Jun 2020 for PLOS ONE
    de-identified data of SSM on 40 participants ending Jun 2020 for PLOS ONE
    [Deidentified_Dataset_for_Validation_Cohort_40_ PLoS 10.08.2020.xlsx]
2020-12-18 De-identified dataset n8 Production Paper
    PONE
    [PLOS_manufacturing_deidentified_12.15.2020.xlsx]
